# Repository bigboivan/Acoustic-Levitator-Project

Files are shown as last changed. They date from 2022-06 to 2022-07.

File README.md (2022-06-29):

# Acoustic-Levitator-Project
This is the project I did for Professor Alexandra Navrotsky Lab with fellow undergrad Nicholas To at Arizona State University under the guidance of Dr. Sergey Ushakov. The device is called an Acoustic Levitator which uses numerous ultrasonic speakers or transducers aligned across two arrays to produce enough physical force to levitate a sample. The device was modeled mostly on the TinyLev design created by Asier Marzo,  Adrian Barnes, and Bruce W. Drinkwater. We also had a lot of correspondence and assistance from Victor Contreras. We also built two of Marzo's BigLev levitator models. Nicholas built the first and helped with the second build. I then built the TinyLev and found that it offers the best performance. The material developed by others that was used directly or for inspiration is credited. Feel free to ask questions. 


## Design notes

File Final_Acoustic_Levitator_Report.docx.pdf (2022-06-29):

Final Report on Acoustic Levitator Construction Ivan Matyushov, Nicholas To, Dr. Sergey Ushakov Arizona State University June 28, 2022

1. Summary/Specs
This is my official report of my findings and method of use for the Arduino-based Acoustic Levitators, BigLev and TinyLev, as first proposed by Azier Marzo, Victor Contreras, James Drewitt, and various other collaborators. For optimizing the levitators, current was the most important factor to minimize. This was achieved by altering the distances between the cavities and changing the OCR1A number. Optimizing the amplitude peak-to-peak voltage from the transducers was also important as that tended to improve levitation by generating a stronger pushing force. Increasing the amplitude peak-to-peak voltage was achieved by also optimizing the OCR1A and testing the transducers with an oscilloscope to take out the weakest transducers and keep the strongest. Besides the optimal specs for the levitator, this report explains how to operate, assemble, and configure the acoustic levitators with helping images. Also, it provides graphs and specific data for our findings. In our lab, we made 3 acoustic levitators, two BigLev models and one TinyLev model. We found the TinyLev to provide the best performance. The BigLev models can be found on the Instructables page linked below. We have the necessary TinyLev models as files on the GitHub repository.
2. Introduction and General Assembly
The combination of acoustic levitation with laser heating was developed originally by Intersonic corporation on contract from NASA. It involved stabilizing the sample levitated in the gas jet by six Langevine horn-type custom-made acoustic transducers. During the last 30 years, two commercial instruments were produced in the USA and operated in Germany and Japan for high-temperature research on oxide melts. Marzo publication [3] of multi-transducer acoustic levitation design and open sharing of software and sources for the components lead to rapid employment of acoustic levitators in several research groups (Drewitt, others [1]. Using Marzo’s design, acoustic levitation of Hg (13.6 g/cm3) without any support by gas jets was demonstrated [1].
For a general assembly of the acoustic levitators, the instructables link at the end can be viewed. For the TinyLev, we used metal rods with shaft collars to hold the cavities up and adjust the distance between the cavities. For the BigLev, we cut the holders in the original BigLev 3D model off and printed out the BigLevLip models to attach to the acoustic levitators and enable three rods to be used with shaft collars. To put together the circuit models, wee used screws where the holes are to both put together the circuit holder and enclosure along with securing the driver board.
3. BigLev Specs
Primary Items:

- Transducers: Taidacent OD 16mm 40khz Transducers High Sensitivity Ultrasonic Transducer Ranging Probe RT Split Ultrasonic Transceiver Sensor
- Controller Board: ELEGOO Nano Board CH340/ATmega328P Without USB Cable, Compatible with Arduino Nano V3.0 (Nano x 3 Without Cable)
- Driver Board: L298N Motor Driver Controller Board Module
- Full Shopping list is included in the GitHub repository.
Best operating specs:
- Operating Voltage: 5-25V(refrain from going past 20 V for more than a few minutes as the heat sink gets quite hot)
- Current range: ~0.30 - 0.65 A
- Distance (red BigLev): 111.50-112.50 mm or 164.5-165.5 mm
- Distance (white BigLev): The best distance I found was between 144-146 mm
- 0CR1A: 191
4. TinyLev Specs
Primary Items:
- Transducers: Manorshi Electronics MSO-A1040H07T
- Same things for everything else; only the transducers are different
Best operating specs:
- Operating Voltage: 5-25V (same concern with overheating and high voltage)
- Current range:
- Distance: From both tests, 53-54 mm and 34-35 mm are the best ranges where lowest current was seen. 42-43 mm may also work well. Was successful at levitating Al2O3 and ZrO2 at 55.07 mm of separation.
- 0CR1A: 191
- Levitation of 2mm Al2O3 on TinyLev witnessed at 55.93 mm, 19.6V and 0.51 A. For 55.07 mm, levitation 2mm sized Al2O3 witnessed at 11.9 V, and 3mm ZrO2 was levitated at 19.6V.

Manual/Standard Operating Procedures - Acoustic Levitators

This part of the document is the overview troubleshooting manual for the acoustic levitators. It will detail how to set up, configure, test, and use the acoustic levitators. Much of this document will revolve around helping to yield the best performance out of the acoustic levitators. As I, Azier Marzo, and his associates have found, the acoustic levitator performs best when it is able to operate fully at a high amplitude and as low of a current as possible. This optimal performance can be achieved through a combination of settings.

Section 1: Configuring the Software:
- Updating the code
The code for the acoustic levitators was written for the Arduino circuit and thus operates only in the Arduino IDE program. The code mostly consists of commands for the pins and board, but there is a small variable of the code that can be altered to dictate the frequency and current of the acoustic levitators. Below is the line to look out for:

The variable to change is the 0CR1A. The 0CR1A number has an inverse relationship to the frequency of the transducers as the frequency is approximately 8 MHz divided by whatever number you have for your 0CR1A (Frequency = 8MHz/OCR1A #). For example, with 191 as the 0CR1A, you will have a frequency of around 41.8 kHz. At a value of 200, your frequency will be 40 kHz. The 0CR1A also alters the current and the amplitude of the transducers. Changes in current can be seen just by measuring the current after each subsequent change in the 0CR1A. For the acoustic levitators, we found an 0CR1A of 191 to be ideal as it gave the best amplitude along with a lowered current. Measuring and testing the amplitude is discussed in Section of the manual. The best 0CR1A values tended to be between 190 and 200.
- Uploading the code & Troubleshooting
To upload the code, simply plug a USB into the Arduino board and click on the ⇨ button to upload the code. Any changes can be saved with the ⇩ button.

To ensure the code is uploading to the right place, you may need to configure the drivers for the software and select the board it goes to. This can be done in Tools > Board > Board manager. For this levitator, we downloaded the Arduino AVR Boards driver. Also, at the top left, there’s a drop down menu to select the correct board being used. For the acoustic levitator, we used an Arduino Nano board. Other issues that may arrive could be with the COM port. In Tools > Port, one can choose what USB port the code is sent through. Make sure the Arduino board is connected to the correct port.

Section 2: Connecting/Wiring the Acoustic Levitator
- Connecting the acoustic levitator
The Acoustic levitator has 3 ports to connect to. The cut-out slot on the bottom side of the levitator is for the USB to connect to the Arduino Nano board. The circular male port is for the female DC power supply connector. The blue DB-9 connector is for the acoustic levitator to connect to.

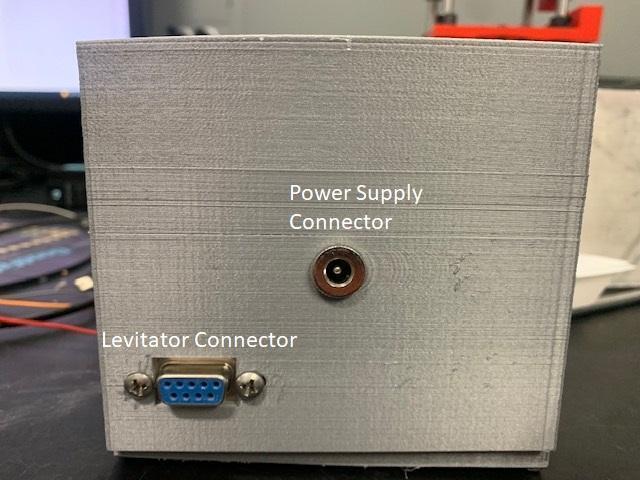
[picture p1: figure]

- Wiring the acoustic levitator In case the wires come loose or changes need to be made, it is important to discuss the wiring of the acoustic levitator. For wiring the acoustic levitator wires to the driver board, you should connect them as follows:

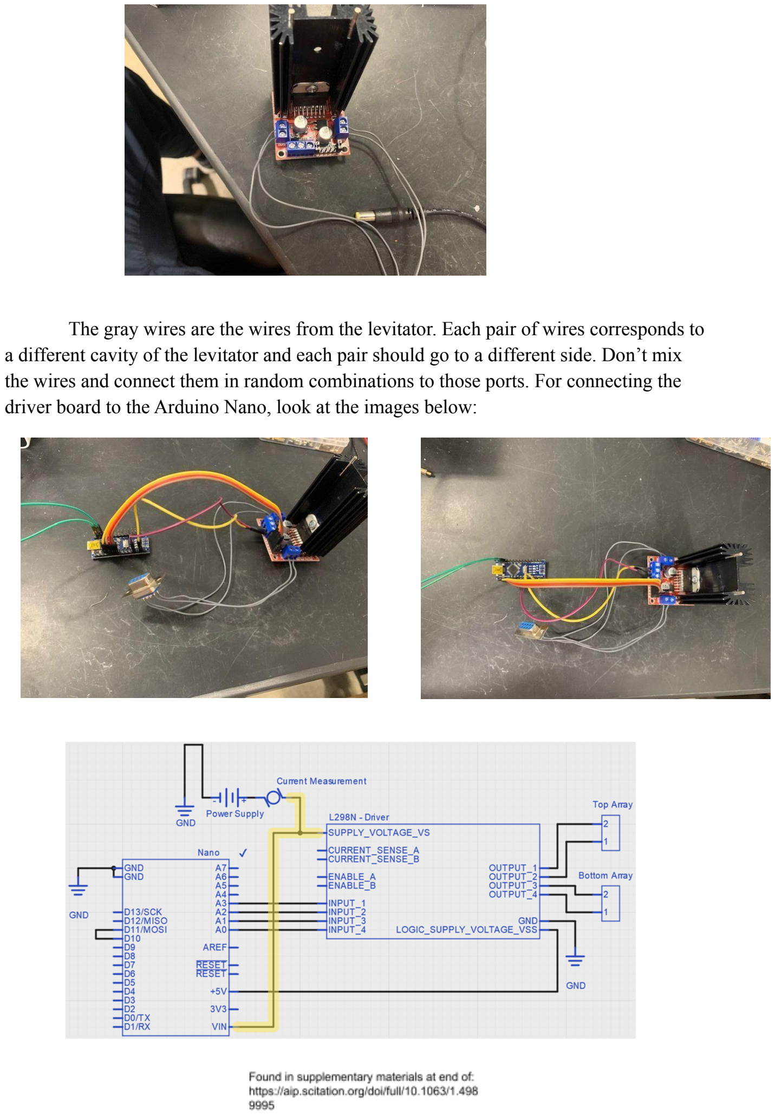
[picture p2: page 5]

The gray wires are the wires from the levitator. Each pair of wires corresponds to a different cavity of the levitator and each pair should go to a different side. Don’t mix the wires and connect them in random combinations to those ports. For connecting the driver board to the Arduino Nano, look at the images below:

In the images of my circuit, the green wire is the connection in the schematic going from D10 to D11. The Bottom array and Top array are the acoustic levitator connections. The purple wire is the connection from +5V on the Arduino board to the right +5V port on the driver board. The singular yellow connector is going from the GND on the Arduino board to the GND connection on the driver board. The multi-colored bundle of four wires, as shown in the schematic, goes from Input 1, 2, 3, and 4, to A3, A2, A1, and A0. The connections for the power supply:

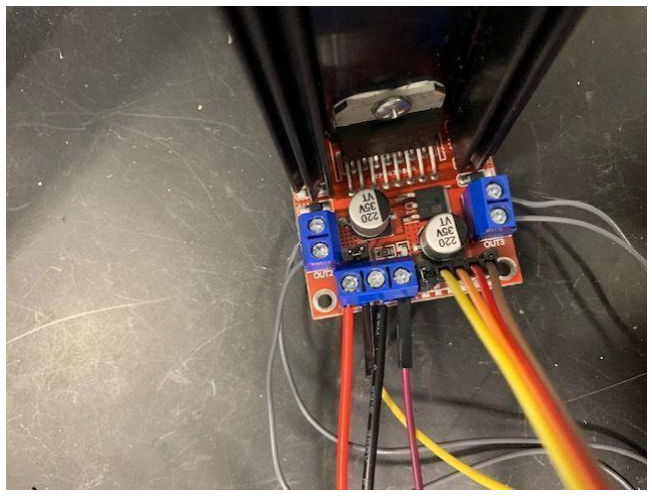
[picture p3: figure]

Here, the black wire from the power supply connector should go to ground with the ground wire from the Arduino, while the red wire goes into the +12V port. As a last note, make sure the screws are tight when assembling the box to make sure the wires stay connected.

Section 3: Testing the Amplitude of the Acoustic Levitator
To test the amplitudes of the acoustic levitator, a handheld Tablet oscilloscope can be used. It gives the amplitudes in V and the frequency in Hz. To start testing, a transducer needs to be wired up to one of the probes like so:

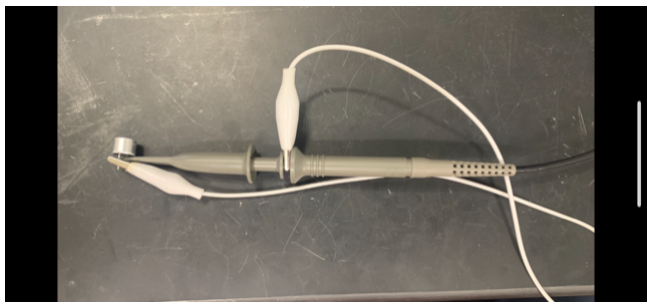
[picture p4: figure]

Doing this allows one of the transducers to act as a microphone while the acoustic levitator outputs sound.

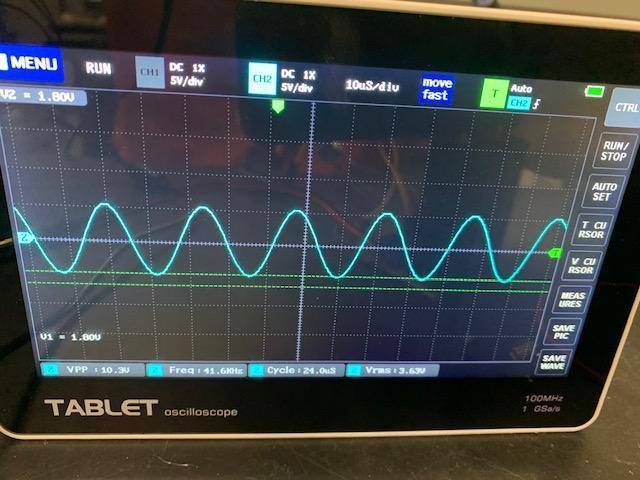
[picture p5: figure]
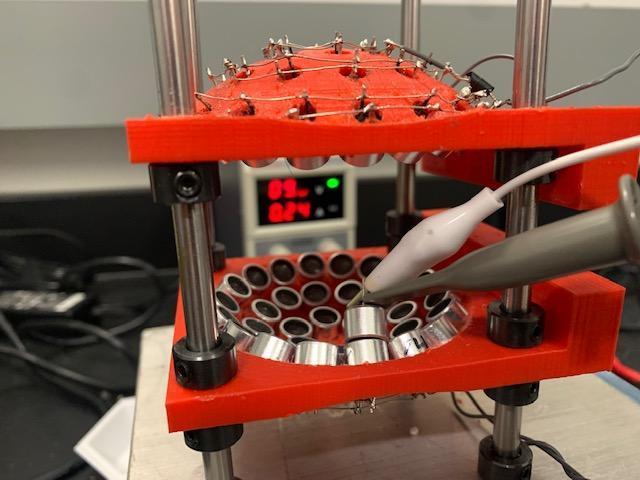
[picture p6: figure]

Putting the oscilloscope probe against the transducer like in the left should get an oscilloscope graph like in the right. On the bottom, there is Vpp, frequency, cycle, and Vrms data displayed. If one goes to measure on the right, the displayed measured values can be selected for each channel. Use the Autoset button to automatically adjust the axes and adjust them to the oscilloscope data produced by the levitator. Testing the amplitude can also be done to ensure that the transducers did not break or that one of the acoustic levitator connectors is disconnected.

Section 4: Configuring the Correct Distance for the Acoustic Levitator
One of the main factors in getting good levitation performance is setting the levitator to correct distances where the sound waves from the transducers will produce a standing wave. This distance needs to be quite precise and small differences away from that distance can make the levitator’s performance much worse. To gauge the correct distance, the current can be measured with a multimeter. Points of lowest current indicate the best distance for optical performance. To measure the current with a multimeter, it can be set up like so:

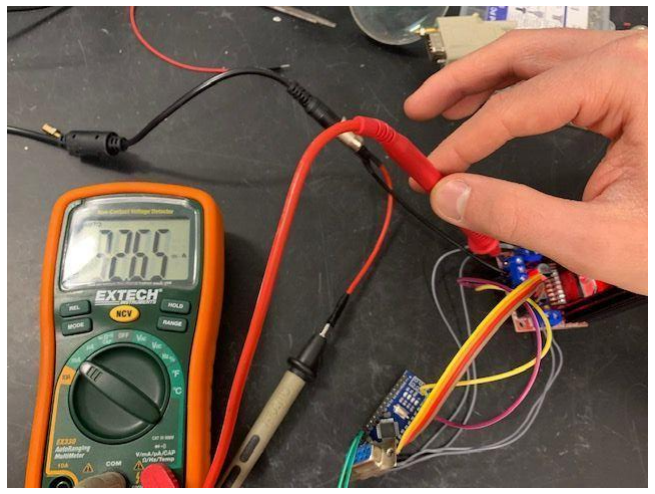
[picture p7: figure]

Here, like the schematic shown in section 2, there is a multimeter in between the red cable’s connection to the +12V connection on the driver board. To set this up, the red cable can be taken out and connected to the black probe of the multimeter, and then the red probe goes into the +12V port of the driver board. To make sure the current is flowing and being measured, set the multimeter to measure mA. Doing this will turn the driver board on and measure the current. From here you can see how distance changes change the current in the multimeter. To change the distance precisely, I took washers and stacked them on the black collars then put the levitator cavities on. For the TinyLev, I obtained these distance charts from 2 different tests:

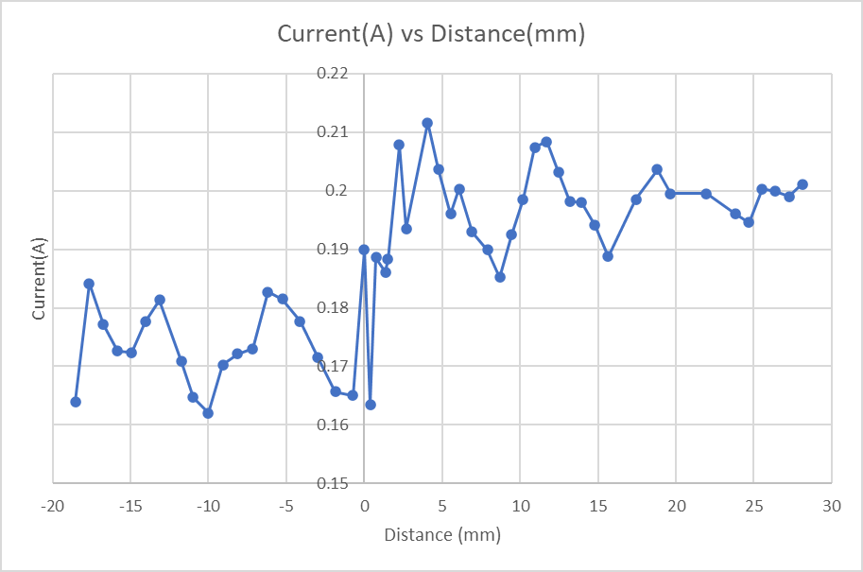
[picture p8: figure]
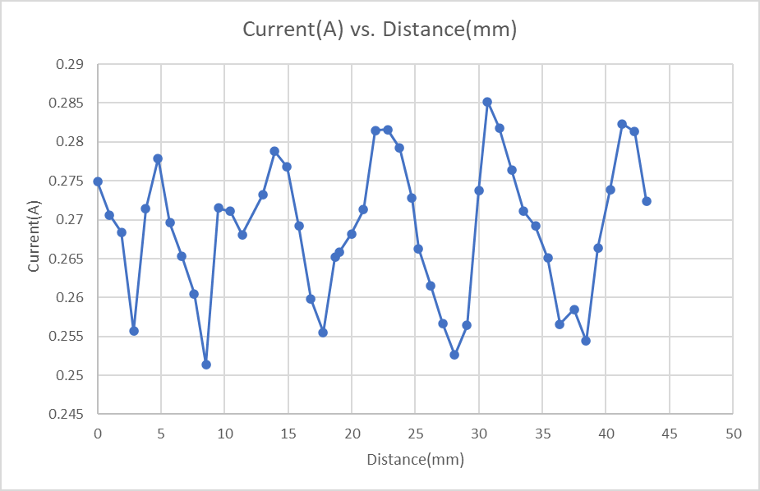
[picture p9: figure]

I found the best distances for the TinyLev to be at 53.4 mm, 42.98 mm, and 42.03 mm from
my own tests. These distances were obtained by measuring the distance from the innermost part of the top cavity to the innermost part of the bottom cavity with a caliper. In the graph, the x-axis is in mm with zero being a distance of 53 mm where I originally started measuring from, so the current can shift within mm and thus the performance can drastically change within a few mm. For distance tests on the BigLev I obtained the following graphs:
White BigLev:

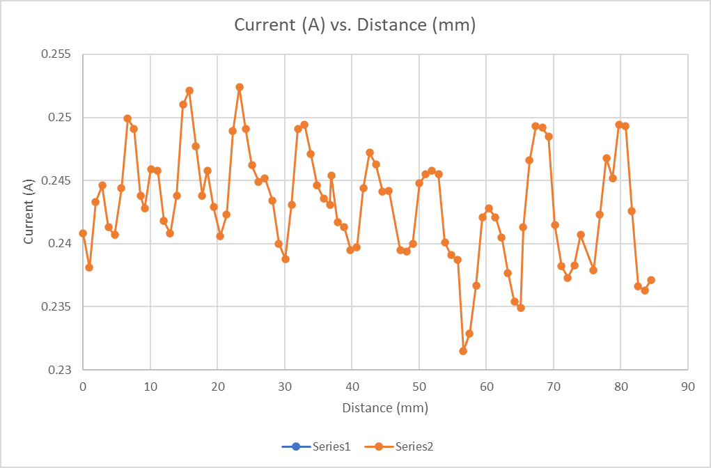
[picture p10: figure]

RedBigLev:

For the Red BigLev, I found that distances of 111.50-112.50 mm or 164.5-165.5 mm worked best, while as for the White BigLev, I found that distances of 144-146 mm worked best.

Section 5: Optimzing our Acoustic Levitator build
To improve our levitators from the initial first BigLev build, Nicholas and I ran some tests on the transducers and the OCR1A# to ensure we were optimizing the build as much as possible. To start, we did tests of OCR1A# and frequency to see the effect of OCR1A# on the frequency. The following graphs display the trends we saw:

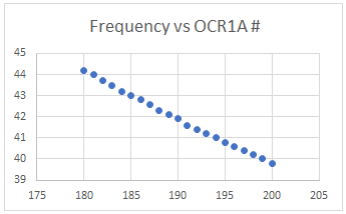
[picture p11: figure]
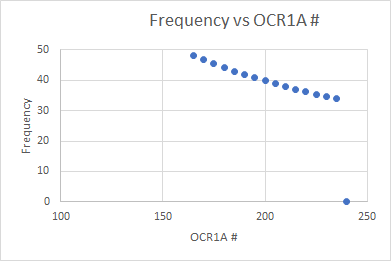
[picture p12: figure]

Similar to the frequency vs OCR1A graphs, these graphs show the peak values of Vpp based on the OCR1A number at 5(left) and 1(right) increments. On both graphs, we found the peak Vpp to occur at an OCR1A number of 190. I did the tests at single, more precise increments to confirm the peak was really at 190. This data helped us the most as it showed us where the signal is going to be proportionally the strongest. Based on this data, we saw that an OCR1A of 190-192 was good. The voltage of the power supply and the transducer used were fixed.

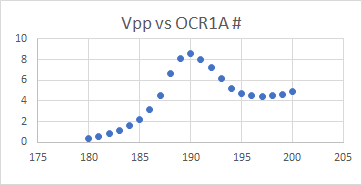
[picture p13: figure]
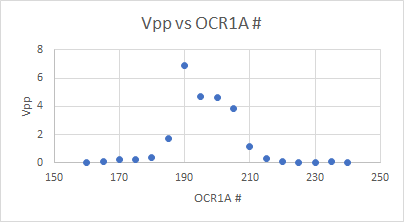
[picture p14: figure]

Lastly, we performed current tests to narrow down the best OCR1A# and hit that necessary minimum current that we desired. From these tests we got the following chart:

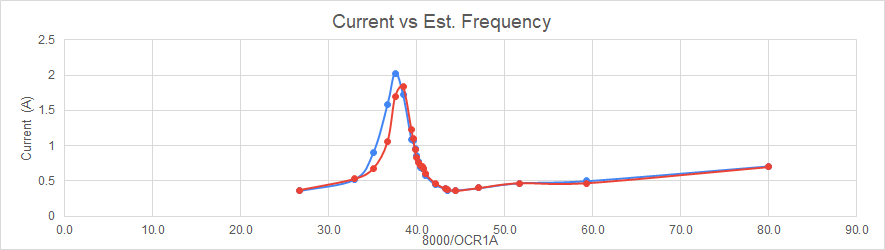
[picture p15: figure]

Since an OCR1A# of 191 yielded a lower current at a good Vpp output, we decided on 191 as the best OCR1A#. Beyond these tests, we also used the oscilloscope tests described previously to test each transducer that we ordered and select for the best performing ones to put onto the levitator. We noticed many of the transducers had noticeable differences in amplitude outputs that we could not jst randomly pick the transducers and place them onto the cavities. Upon doing these prior tests, we assembled the levitators with the strongest transducers in the center and the weakest ones along the outermost of the cavities. On the red BigLev, it was apparent that at 10V of power, the transducers on the outer rim had amplitudes of ~5V, while the centermost transducers had amplitudes of ~7.5V. For the TinyLev, the transducers had amplitudes of ~12-15V from the outer to the center rims. For both levitators, the transducers were operating at frequencies of 41.3 kHz.
Section 6: References and Sources
1. https://aip.scitation.org/doi/full/10.1063/1.4989995
2. https://en.wikipedia.org/wiki/Ultrasonic_transducer
3. https://www.instructables.com/Acoustic-Levitator/
4. https://en.wikipedia.org/wiki/Standing_wave
5. https://en.wikipedia.org/wiki/Acoustic_levitation
6. https://brucedrinkwater.com/2016/06/11/acoustic-levitation-in-the-microgravity-of-space/
7. https://brucedrinkwater.com/portfolio/how-to-make-an-ultrasonic-levitator/
8. https://www.youtube.com/playlist?list=PLGMLYoMGTMH7K6_e_75AVECkDAZz7QSKi
9. https://aip.scitation.org/doi/10.1063/5.0013347
10. Victor Contreras’ email: victor@icf.unam.mx

Section 7: Further Reading
1. Asier Marzo’s available Publications: https://aip.scitation.org/author/Marzo%2C+Asier
2. https://hackaday.com/tag/acoustic-levitation/
3. https://www.nature.com/articles/s41598-020-60978-4

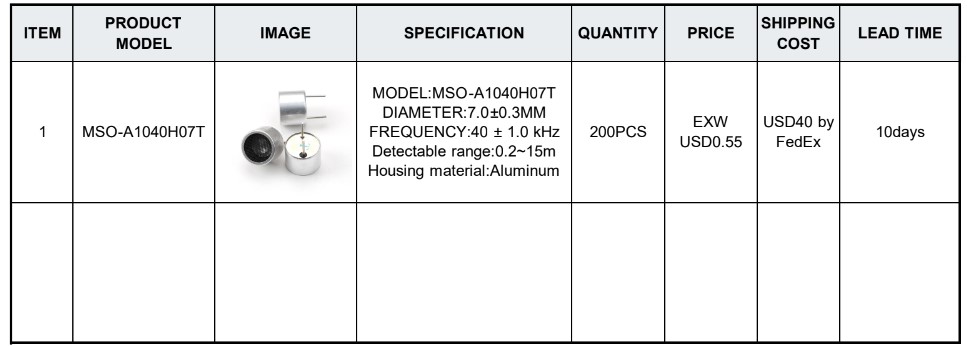
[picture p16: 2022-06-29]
TinyLev_transducers_quote.jpg

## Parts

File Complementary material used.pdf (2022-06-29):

Tablet Oscilloscope:
https://www.amazon.com/Oscilloscope-Bandwidth-Sampling-Multifunction-Portable/dp/B08KVVXFHV/ref=asc_df_B08KVVXFHV/?tag=hyprod-20&linkCode=df0&hvadid=475770909319&hvpos=&hvnetw=g&hvrand=15186959441463408141&hvpone=&hvptwo=&hvqmt=&hvdev=c&hvdvcmdl=&hvlocint=&hvlocphy=9060222&hvtargid=pla-1028155501586&psc=1 (https://www.amazon.com/Oscilloscope-Bandwidth-Sampling-Multifunction-Portable/dp/B08KVVXFHV?hvadid=475770909319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)

DC Power Connectors for the Circuiting holder and enclosure: https://www.amazon.com/Socket-Threaded-Connector-Adapter-Dustproof/dp/B08SJM2G52/ref=sr_1_10?crid=17FIIZMPWZA6N&keywords=DC+power+connectors&qid=1656428167&sprefix=dc+power+connectors%2Caps%2C63&sr=8-10 (https://www.amazon.com/Socket-Threaded-Connector-Adapter-Dustproof/dp/B08SJM2G52)

DB9 connectors to create a port for the Acoustic Levitator wires and the driver board to communicate through:
https://www.amazon.com/Pc-Accessories-Connectors-Connector-20-Pack/dp/B014IVD7L0/ref=sr_1_11?keywords=db9+connector&qid=1656470162&sr=8-11 (https://www.amazon.com/Pc-Accessories-Connectors-Connector-20-Pack/dp/B014IVD7L0)

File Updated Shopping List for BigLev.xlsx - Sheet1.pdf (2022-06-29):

Name | Supplier
uxcell 5pcs PCB DIY DPDT 3 Position Mini Slide Switch AC 250V 3A 125V 6A | uxcell
L298N Motor Driver Controller Board Module, 3 PCS | SongHe
6400BG | AAVID
Heatsink Compound | Sparkfun
ELEGOO Nano Board CH340/ATmega328P Without USB Cable, Compatible with Arduino Nano V3.0 | ELEGOO
HGJI 60W Adjustable AC/DC Adapter Switching Power Supply 100-240V to 3.3-24.7V 2.5A 50-60hz... | abovehill
E-outstanding 5PCS PCB Mount DC005 5.5 x 2.1 mm Female 3Pin DC Power Connector Socket Jack Plug | E-outstanding
USBMINI 3ft USB2.0 A Male to Mini-B 5Pin Male | CircuitSpecialists
EDGELEC 120pcs Breadboard Jumper Wires... | EDGELEC
KAIWEETS 10PCS Electrical Alligator Clips with Wires Test Leads Sets Soldered and Stamping Jumper Wires... | KAIWEETS
12 AWG Wire, SHONSIN 12 Gauge Silicone Wire 100% Copper【10ft Red & 10ft Black Separated】... | SHONSIN

304 Stainless Steel Woven Wire Mesh #80 Mesh - Hole 0.18mm...

Break Away Single Row Round Headers Machine Pin...
Taidacent OD 16mm 40khz Transducers High Sensitivity Ultrasonic Transducer Ranging Probe RT | Taidecent

This list should be enough to create 3 levitators. It, however, does not include shipping fees and taxes.

Quantity | Price ($ * quant) | Website
1 | 7.99 | Amazon
1 | 8.99 | Amazon
3 | 4.56 | Newark
2 | 4.5 | Sparkfun
1 | 13.99 | Amazon
3 | 53.97 | Amazon
1 | 5.99 | Amazon
3 | 3.42 | CircuitSpecialists
1 | 5.79 | Amazon
1 | 5.59 | Amazon
1 | 9.36 | Amazon
1 | 11.77 | Amazon
1 | 7.99 | Amazon
300 | 99 | Alibaba
Total = | 242.91

https://www.amazon.com/5pcs-DPDT-Position-Slide-Switch/dp/B00XBG6IMO

https://www.amazon.com/Controller-Module-Bridge-Stepper-Arduino/dp/B07RB2LWD7

https://www.newark.com/aavid-boyd/6400bg/heat-sink/dp/18M8220 (https://www.sparkfun.com/products/9576)

https://www.sparkfun.com/products/9599https://www.amazon.com/ELEGOO-Arduino-ATmega328P-Without-Compatible/dp/B0713XK923

https://www.amazon.com/Adjustable-Adapter-Switching-100-240V-3-3-24-7V/dp/B07T2SFGHN

https://www.amazon.com/outstanding-Mount-Female-Connector-Socket/dp/B07SR9159S

https://www.circuitspecialists.com/usbmini.htmlhttps://www.amazon.com/EDGELEC-Breadboard-Optional-Assorted-Multicolored/dp/B07GD2BWPY

https://www.amazon.com/KAIWEETS-Electrical-Alligator-Connection-Experiment/dp/B07WQ21YMY/

https://www.amazon.com/Shonsin-Silicone-Flexible-Conductor-Available/dp/B085HWRJ3M/https://www.amazon.com/SZONEE-Stainless-Steel-Woven-0-18mm/dp/B085W62K71

https://www.amazon.com/Single-Headers-Machine-Female-2-54mm/dp/B0187LTEX2https://www.alibaba.com/product-detail/Taidacent-OD-16mm-40khz-Transducers-High_62420887332.html?spm=a2700.galleryofferlist.normal_offer.d_title.7bcd67850VbcDf

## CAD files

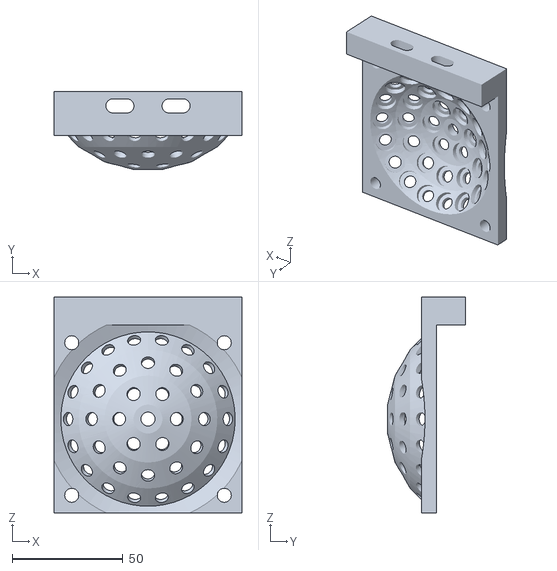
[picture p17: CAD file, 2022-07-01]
TinyLev_R47mm con soporte (3) (2).STL
85.0 x 35.3 x 97.7

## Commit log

2022-06-28 3D Models used
    The circuit holder and circuit enclosure files are the parts I 3D printed to contain my acoustic levitator circuiting for better organization and presentation. The BigLevLip file is a lip I attached 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
    [BigLevlip (1).STL, BigLevlip.SLDPRT, circuit_enclosure.SLDPRT, circuit_enclosure.STL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]
2022-06-28 Add files via upload
    3D models of the circuit holder and enclosure go together and can be screwed together once printed. They will hold and organize the acoustic levitator circuit together. The BigLevLip is a model I use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
2022-06-29 Add files via upload
    Here is the report I put together for my project. This focuses on mostly what we did and the differences from what Asier Marzo and some other colleagues have done. The links at the end of the report 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
2022-06-29 Add files via upload
    These are the models for the 3D printed circuit boxes and the BigLev lip attachments we used to turn our original BigLev 3D models into adjustable levitators supported by three rods.
2022-07-01 Add files via upload
    This is the file for the cavities of the TinyLev. Print out two of these for full top and bottom sides of the levitator.
    [TinyLev_R47mm con soporte (3) (2).STL]
